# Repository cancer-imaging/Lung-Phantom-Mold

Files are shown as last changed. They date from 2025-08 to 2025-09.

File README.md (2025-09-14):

This repository contains the fabrication instructions and 3D printing STL model to reproduce the agar-intralipid lung mimicking phantom described in [INSERT DOI WHEN AVAILABLE]
We recommend printing the mold using a fused filament device (we use the Bambu P1S) with PLA (Bambu basic), to facilitate cutting and removal of the lumen cone.

Journal Article Abstract:
Significance: There is an unmet need for readily accessible imaging targets to verify whether devices can discriminate lesions from healthy tissue and identify sub-surface vasculature in the small airways.
Aim: Develop a phantom that mimics human segmental airway adenocarcinoma in vivo for 1310 nm endoscopic optical coherence tomography (OCT) and angiography characterization.
Approach: We develop phantoms using a mixture of agar, intralipid, and coconut oil cured in a 3D printed mold with embedded tubing to mimic vasculature. The parenchyma optical attenuation coefficient (OAC) is calibrated using optical transmission measurements from an agar and intralipid dilution series. Depth resolved OAC histogram distributions, analysis of variance, and image quality are used to assess repeatability and biofidelity of these phantoms.
Results: Transmission measurements show large increases in OAC when intralipid is cured with agar compared to water-intralipid dilutions. Representative phantom OACs show repeatability within 2.7% and match normal in vivo tissue measurements within 16%. Embedded lesion phantoms achieve imaging characteristics of in vivo adenocarcinoma. Fluid flow within embedded tubing is visualized with Doppler OCT. 
Conclusions: The segmental airway phantoms demonstrate in vivo human imaging characteristics, including structural and optical markers of pathological progression - providing a platform for imaging system characterization and optimization.

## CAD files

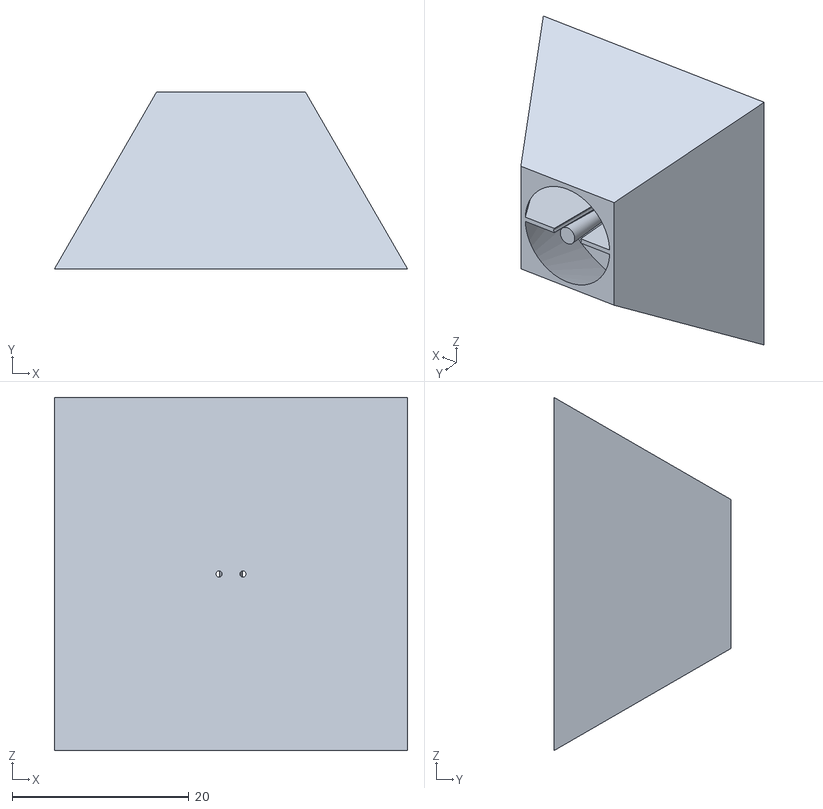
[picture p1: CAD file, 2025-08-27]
Phantom Mold.STL
40.0 x 20.0 x 40.0

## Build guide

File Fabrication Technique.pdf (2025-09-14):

# Supplemental Material

# Segmental airway phantom preparation procedure

Equipment
- Hot plate
- Thermometer
- 2x250 mL borosilicate beaker
- 50 mL graduated cylinder
- Top loading balance
- Disposable scoop
- 18 G 1” blunt needle
- 26 G 1/2” blunt needle
- 3x5mL syringe
- 2x5cm 0.021”ID, 0.003” Wall PET tubing (021-0030 PET01. Nordson Medical. Salem, New Hampshire)
- Swab
- Tweezers
- Scalpel
- 1/8” round precision file
- UV-cure epoxy (NOA 63. Norland Products Inc. Jamesburg, New Jersey)
- UV curing lamp (Liquid light guide allows for improved flexibility)
- Refrigerator (4°C)

Reagents
- Agar powder (05039 Agar. MilliporeSigma Canada Ltd. Oakville, Canada)
- Intralipid (Intralipid® 20%. Fresenius Kabi Canada Ltd. Toronto, Canada)
- Coconut oil (Organic virgin coconut oil, cold pressed & unrefined. Nutiva. Richmond, California)
- Deionized water

Table 1. Materials for normal and lesion lung tissue mimicking phantom solutions using OCT at 1310 nm

Reagent | Normal | Lesion
Agar powder | 0.5 g | 0.5 g
Coconut Oil | 3.0 mL | 3.0 mL
Intralipid®20% | 2 mL | 0.5 mL
Deionized Water | 45 mL | 45 mL
Total | 50.5 mL | 49 mL

Procedure
Prepare 4 moulds.
1. 3D print moulds using filament printer
a. STL available at: https://github.com/cancer-imaging/Lung-Phantom-Mold
2. Examine lumen cone to ensure matrix will not be damaged when cone is extracted.
3. File internal surfaces to remove “stringing”.
4. Using dental pick, open holes in bottom of mould to ensure PET tubing can be inserted.
5. Rasp front edges of tubing supports to remove burrs.
6. With UV cure epoxy:
a. Insert PET tubing into hole, position against support, with ~ 1cm extending out either end of mould
b. Tack tube in position with small amount of epoxy and cure epoxy.
c. Secure in position, applying epoxy along length of tube and cure epoxy.
d. Seal around perimeter of tube on external bottom face of mould (so matrix cannot escape via tube port) and cure epoxy.

Prepare matrix:

7. Heat up hotplate to 300ºC.
8. Using scale and disposable scoop, tare to beaker #1 and dispense 0.5 g of agar.
9. Scoop ~5 mL of coconut oil into beaker #2, place on hotplate, stir until melted. Fill syringe #1 with 3 mL coconut oil.
10. Dispense 45 mL of deionized water into graduated cylinder.
11. Attach 18 G 1” blunt needle tip to syringe #2; fill with intralipid from IV bag (refer to table 1; if implanting lesion use 0.5 mL or for normal matrix use 2 mL).
12. Combine coconut oil, distilled water, intralipid into beaker #1 containing the agar.
13. Heat beaker #1 to 95ºC, stirring intermittently, then remove from hot plate.
14. If implanting lesion:
a. Pull ~2 mL of lesion solution into syringe #3.
b. Place small droplets on lumen cone.
c. Return remaining solution in syringe to beaker #1.
d. Place moulds into fridge for 5 minutes.
e. Add remaining intralipid (1.5 mL) to beaker to create normal matrix solution.
f. Reheat to 80ºC then remove from heat.
15. When mixture cooled to 60ºC, extract into syringe #3.
16. Dispense matrix into moulds (should fill 4 moulds). If needle tip becomes blocked, immerse in beaker 1 to remelt.
17. Place in fridge immediately.
18. Allow to cure for >4 hours or preferably overnight before imaging. Phantoms maintain their properties for approximately 48 hours from when they are first placed in the fridge.

Prepare phantoms for imaging:

19. Use scalpel to cut around perimeter of lumen at bottom face, being careful to not damage tubing.
20. Use tweezers to push lumen cone out top surface of matrix, then extract, being careful not to damage matrix.
21. Insert 26 G ½” blunt needle into one tube, epoxy into position using Norland 63.

Table 2. Record of phantom batches

Batch # | Description | Sample Number
Batch start time: | Placed in fridge:

Total Samples

Table 3. Record of Images collected

Batch: | Time removed from fridge:
Sample | Probe # | Imaging Time | Pullback #

Time returned to fridge:
